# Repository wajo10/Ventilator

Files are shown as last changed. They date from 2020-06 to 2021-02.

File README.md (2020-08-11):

# RespiraWorks Open Source Ventilator












This is a common repository for all hardware and software components of the RespiraWorks open source ventilator project.

**If you intend to contribute, please read our [wiki](https://github.com/RespiraWorks/Ventilator/wiki).**

[RespiraWorks](https://respira.works/) is a 501(c)(3) non-profit organization with over 100 contributors worldwide
working to rapidly develop, manufacture, and deploy a low-cost and open-source ventilator for communities under-served
by the global supply chain.

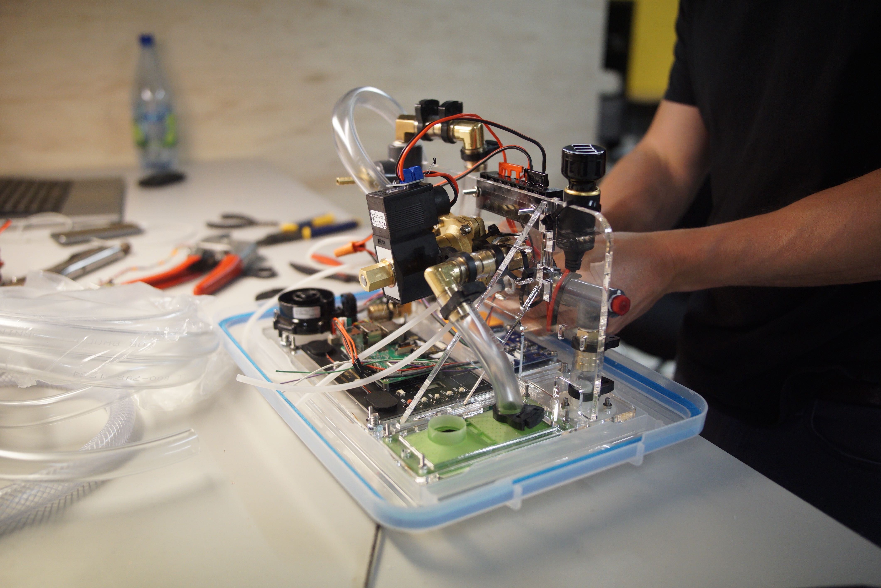
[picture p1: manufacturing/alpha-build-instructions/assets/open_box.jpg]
Ventilator under construction


## Design Origin

Most low-cost ventilator designs tackle the 'bridge' - how to keep a patient alive for 6-8 hours of closely monitored
care until they can be transitioned to a full ventilator. However COVID-19 patients require lung-protective adaptive
ventilation strategies, and require ventilator support for days to weeks.

Early in the crisis, we realized that the ventilator designs that could be completed in weeks might not be necessary,
and if so, a more feature complete ventilator would be needed. Despite constant developments in the disease progression,
we realized that a true-open source ventilator, with transparent requirements, design history documents, and yet still
optimized for low-cost and ease of manufacturing would enable expanded global access to a critical piece of medical
equipment.

Our ventilator exists between the short-term ambu-bag actuating designs and the commercial ventilators offered by
established manufacturers. It provides essential features such as a graphical user interface, adaptive pressure
controls, and fine control of FiO2, oxygen, and PEEP, with CMV, SIMV, PSV and PRVC operating modes. Unlike traditional
ventilators, our design work is being completed as fully open-source design, yet still with an IEC-conformant quality
process, and an optimized BOM for sourcing and manufacture worldwide.

Our target is not the US or Europe, but the middle- and low-income parts of the world that will deal with COVID-19 for
longer, with less healthcare, and a larger deficit of medical devices. RespiraWorks provides solutions for these
communities where existing manufacturers cannot.

## DISCLAIMER

**This is an incomplete, as yet untested design that is not yet intended to be used on patients.**

**This repository contains live documents. There are duplicate and alternative items for undecided aspects of the
physical design. Components may or may not connect and integrate as intended. Contents may also be out of date. If you
decide to buy or build anything, do so at your own risk.**

## CoVent Documentation

A set of comprehensive documents denoting the current state of the ventilator design, manufacturing and assembly specs,
was created for the CoVent competition in June 2020. Links to key documents follow. This is more detailed than the
documentation contained in the repository, but note that it is also a snapshot in time as of late June 2020.

* [Design Overview document](design/assets/covent-june-2020-design-overview-document.pdf)
* [Progress Status Report](design/assets/covent-june-2020-progress-status-report.pdf)
* [Assembly instructions](manufacturing/assets/covent-june-2020-assembly-instructions.pdf)
* [Manufacturing for custom components](manufacturing/assets/covent-june-2020-production-methods-for-custom-components.pdf)

## Repository Structure

* [System Requirements](requirements) -
  describes the requirement architecture, hierarchy, and process. Links to the releases of our system requirements, hardware specifications, and software requirements.
* [Ventilator Design](design) -
  describes the functional implementation and design theory of the system. This document also defines the hierarchy for the subsystems below.
    * [Design Rationale](design/design-rationales.md) - An explanation of the rationale that went into specific parts can be found here.
    * [Pneumatic System](design/pneumatic-system)
    * [Electrical System](design/electrical-system)
* [Manufacturing design](manufacturing)
    * [Alpha Build Instructions](manufacturing/alpha-build-instructions) - documentation for building the "Alpha" prototype of the device which can be used by contributors to test and experiment with.
    * [Beta Build Plan](manufacturing/beta-build-instructions) - Details on this page will be added as we progress further into beta build.
* [Printed Circuit Board (PCB)](pcb) - design, materials, assembly instructions, validation code
* [Ventilator Software](software) - Source code for cycle controller and user interface; debug tools, test scripts and test data
* [Research & Development](research-development)
    * [Project: Fan](research-development/project-fan)
    * [Project: IAV Air Control](research-development/project-iav-air-control)
    * [Project: Pinch Valve](research-development/project-pinch-valve)
    * [Project: Venturi](research-development/project-venturi)
    * [Characterization Test Plan](research-development/characterization-test-plan.md)
* [Quality Assurance](quality-assurance)
    * [Testing](quality-assurance/testing)

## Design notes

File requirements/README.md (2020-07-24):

# Requirements

We formally manage our product requirements in
[Valispace](https://covent-19.valispace.com/specifications/requirements)

For access and guide on using Valispace efficiently, see the [Using Valispace](using_valispace.md) page.

Latest exports:
* [PDF format](system-reqs.pdf)
* [XLSX format](system-reqs.xlsx)
* **#TODO:** export to `json`

## Managing requirements

This is a living document, the entry point for learning how we manage requirements and how to help with that. If you
learn something useful, or if you think this page could be structured better, **please edit this page**.

As usual, where appropriate, **cross-link with other resources**: e.g. Slack threads where a decision was made (or names
of people who made a decision), Github issues tracking certain work etc.

## Are the requirements up to date?

Not yet, but we're trying to get there: many of them need clarification, many are missing, some may be vague or
redundant. If something looks off, it probably is - please do your part to clarify it and edit the requirement - see
below how.

## Is everything in Valispace?

As of May 19, system and software requirements have been transferred from various spreadsheets on Google drive.
The deprecated sources of this transfer are available for reference in
[this folder](https://drive.google.com/drive/folders/10EUN9lYFaMPZbI094FU3wP_rDw2_dcRc?usp=sharing).

**TODO:** Have electrical / PCB requirements been transferred?

Some additional artifacts are highly related to requirements or should be cross-linked with them, but are currently not
managed in Valispace:
* **Failure Modes and Effects Analysis (FMEA)** - currently managed in
[this spreadsheet](https://docs.google.com/spreadsheets/d/1qlTV5HqxnhlJXuhbSsEIfU-YwnN6PzgASv9_2dc5-cM/edit#gid=929514620)
  * **TODO:** How do we manage cross-linking between FMEA and the requirements?
  * **TODO:** We should have a wiki page explaining the FMEA
* **Validation logs** - when we have a formal validation effort spun up, we will need to be able to trace every
requirement to logs of tests showing that the requirement is met in a specific version of the product.
* **TODO:** Anything else?

## Where did they come from?

The **system requirements** come from a variety of sources: ISO standards (**TODO:** which ones?), ventilator manuals
(**TODO:** which ones?).

The **software requirements** are a result of people from the Software team analyzing the system requirements from their
perspective and mapping them onto the software architecture
(**TODO:** we should have a page about software architecture).

**TODO:** Where did the other ones come from?

## How will we know that they are correct and complete?

**TODO:** How?

## How will I know when a requirement changes?

**TODO:** How?

## I have a general question about managing requirements

Ask it on `#requirements`. (**TODO:** Are there more detailed places where one should go with more specific questions?
Eg. hardware requirements, legal requirements, what to do if you need to talk to a doctor to clarify something?)

## I need to clarify an existing requirement

Use the Valispace "discussion" feature on the respective requirement.
**TODO:** Describe the feature in more detail, e.g. will I get a notification if somebody responds? Will I get a
notification if somebody asks a question about a requirement I added?

## I need to add a new requirement

If you found out that the system needs to have some important requirement that is currently not tracked, please add it
to Valispace and link it with other related requirements. For example, if you looked at the requirement "must have a
BATTERY LOW alarm" and found that there is no requirement to have a battery sensor, go ahead and add a requirement to
have a battery sensor.

If you're adding a new hardware requirement, ping David Gerson on Slack and let him know.

## Which requirements are higher-priority?

**TODO:** This ideally should link to a well-prioritized "milestones" page

# Cross-cutting TODOs

In addition to the explicitly listed questions on each requirement, a few recurring themes implicitly apply to almost
every requirement. We need to conduct several large-scale requirement cleanups.

* For all requirements we need to know which modes are they relevant to
  * **TODO:** How will we represent this in Valispace?
  * **TODO:** Classify all requirements by modes where appropriate - **should file a Github issue to track this**

* Many requirements talk about displaying a value, or a value being within certain bounds. It is often unclear whether
the value is an instant sensor reading, a computation from the most recent breath, a time series thereof, or an average
over some window (time-delimited or breath-delimited)
  * **TODO:** Audit all such requirements and clarify them -  **should file a Github issue to track this**

* Many values can be "commanded" (i.e. the device is trying to achieve a specific value) and "measured" (i.e. we can
measure what value has actually been achieved). In some requirements it is unclear which modality it is talking about.
  * **TODO:** Apply either "commanded" or "measured" to all magnitudes in all requirements - **should file a Github issue to
  track this**

* Requirements for device performance (how quickly and how precisely the device should achieve commanded values of
different parameters) are incomplete. There is a catch-all of 10% (**TODO:** insert ID for this requirement).
  * **TODO:** Identify such requirements for all necessary parameters - **should file a Github issue to track this**

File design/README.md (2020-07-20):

# System Architecture

-------------

This document contains description of ventilator design implementation and closure of issues which
apply at the system level, such as architecture configuration.

## Overview

A ventilator is a device which supports the breathing of a patient who cannot generate
sufficient respiratory effort to oxygenate their blood. In order to do that, the device
must generate sufficient pressure to overcome the resistance of the lung tissue and the
machine itself. It must vary this pressure over time as the lungs fill and then deflate.
In order to improve oxygenation, ventilators also almost universally apply some
back-pressure to the lungs (PEEP).

There are dozens of ways to design a ventilator and each has trade-offs. This document
describes the series of design decisions that led to the final design implementation
as a means of gaining a finer understanding of the final solution and why it resulted the
way that it did.

The first question is where the ventilator is generating pressure to drive into the lungs.

Displacement type devices provide a mechanical compression of a fixed volume to drive air
into the lungs. These are commonly employed in existing ventilators, and they provide a
high degree of volumetric accuracy and precise control of flow. There are two challenges
here. First is a question of supply chain, the volume of air which must be delivered into
a lung is relatively large, as far as traditional cylinders go. The lubricant and gasket
material must be oxygen compatible, and relatively expensive and sensitive drive
mechanisms are required. The designs end up rather heavy and expensive. Bellows-type
devices can be helpful in addressing the volume issue, but are very challenging to design
for the millions of cycles required, in addition to being difficult to source.

Ventilator Design Overview

[Source](https://docs.google.com/presentation/d/1ye96itSLfdbO9PQT0MSiq6xR2ArqD2MpV1Wj8ORfHeo/edit#slide=id.g7330d84036_1_0)

## Overview Documents

* [Concept of Operations](conop.md)

## Subsystems

**#TODO:** Introduce each subsystem properly

   * [Pneumatic design](pneumatic-system)
   * [Electrical design](electrical-system)
   * **Mechanical design: #TODO**

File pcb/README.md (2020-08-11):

# RespiraWorks Ventilator Mainboard Rev 1.0 

## Important Rev 1.0 PCB Errata
* [#63](https://github.com/RespiraWorks/pcbreathe/issues/63): DNP resistors populated on board, typing 3.3V to the 5V rail (bad) - if you have SN 01, 02, 03, or 05 - don't continue using the board without executing the fix in this issue ticket.  See ticket for rework instructions and photos.  All other serial number boards are shipping with this issue fixed.
* [#64](https://github.com/RespiraWorks/pcbreathe/issues/64): Yellow and Green alarm LEDs don't work due to a pin use conflict on the nucleo
* [#56](https://github.com/RespiraWorks/pcbreathe/issues/56): Blower command is 5V but nucleo outputs 3.3V.  All boards are currently shipping with a level translator fitted which addresses this problem, however the blower will turn on full blast briefly at reset ([#62](https://github.com/RespiraWorks/pcbreathe/issues/62) - to be fixed in next rev)
* [#66](https://github.com/RespiraWorks/pcbreathe/issues/66) I2C sensor connectors labeled A, C, B, D. Should be A, B, C, D :facepalm:  To be clear, what this means is, the I2C multiplexer assignments, as labeled on the board in Rev 1.0 are: MUX0: SENSOR A; MUX1: SENSOR C; MUX2: SENSOR B, MUX3: SENSOR D
* [#846](https://github.com/RespiraWorks/Ventilator/issues/846): anti-miller caps C33 and C34 filter out PWM signal and prevent proper operation.  The Miller effect is only present at startup and doesn't cause a problem with permanently connected loads like the PSOL.  Remove C33 and C34.

## Rev 1.0 PCB Quick Start Guide (visual guide pictures to be uploaded soon)
* If you have SN 01, 02, 03, or 05, make sure you check the errata above before you proceed or you may damange the Rpi.
* Verify that you have an STM32-L452RE module (not an STM32-L452RE-P module, they have different pinouts - see #51)

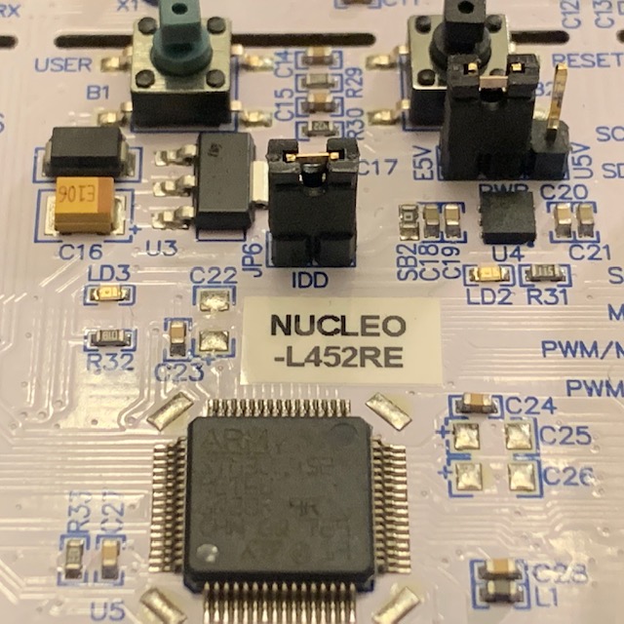
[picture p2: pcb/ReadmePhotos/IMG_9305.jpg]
verify model

* Plug the Nucleo into the PCB, observing the silkscreen (white outline on the board) for correct orientation.

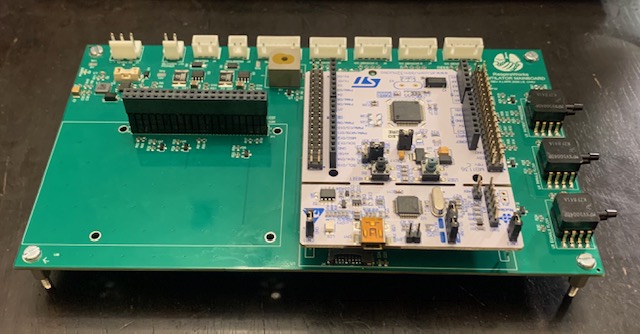
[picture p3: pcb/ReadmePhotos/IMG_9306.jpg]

* Move the JP5 jumper in the upper-middle-center of the Nucleo board to the E5V position.  This tells the board to expect external power from the PCB.  This will avoid programming problems.  If you wish to remove the Nucleo board and work with it on its own without the PCB, move the jumper back to the U5V position to power it from USB.

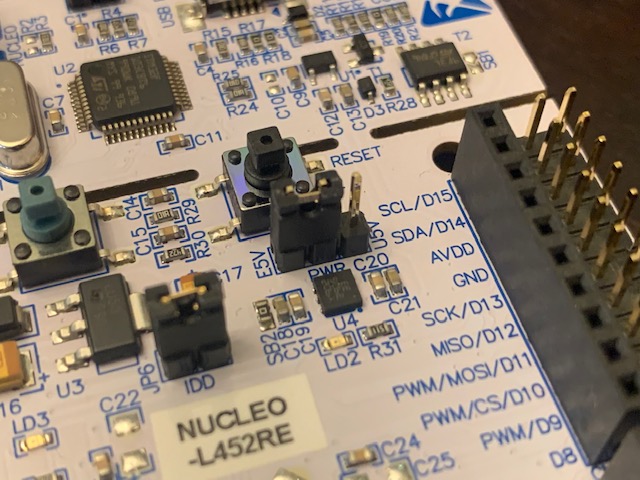
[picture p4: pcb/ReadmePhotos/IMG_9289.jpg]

* If you have a X-NUCLEO-IHM03A1 or X-NUCLEO-IHM02A1 stepper driver accesory, plug that in on top of the Nucleo.  The long gold pins of this module can get bent so make sure they are straight and they all go into their respective sockets successfully.  The stepper driver green connectors go in the direction of the white connectors on the mainboard PCB.  For setting up multiple stepper boards and/or connecting actual steppers, see "Setting Up To Drive Steppers" lower down in this readme.

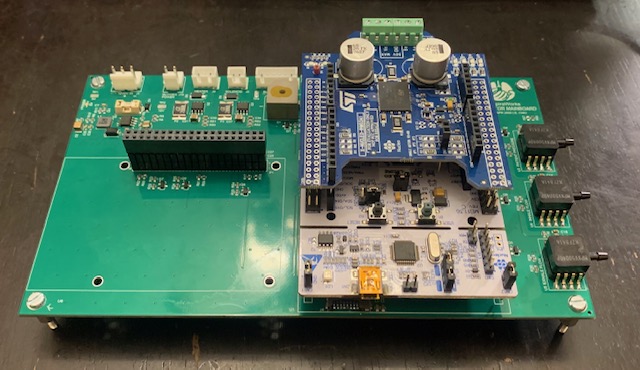
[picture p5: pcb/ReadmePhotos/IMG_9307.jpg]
plug in the stepper driver

* If you are using an Rpi 3B+ or 4 with this PCB, plug this into the RPI socket.  Note that if you have the standoffs fitted, do not overtighen them as this can damage the Pi.

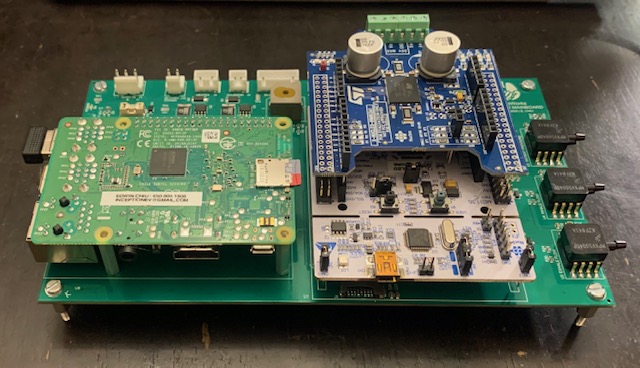
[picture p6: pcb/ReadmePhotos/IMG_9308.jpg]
plug in the Rpi

* If you are using Touchscreen w/ Speakers with your Rpi, connect an HDMI cable (included with Touchscreen package) between the Pi and the Touchscreen.  Similarly, connect a USB micro cable (included with Touchscreen package) between the Pi and the TOUCH+5V connector on the Touchscreen.

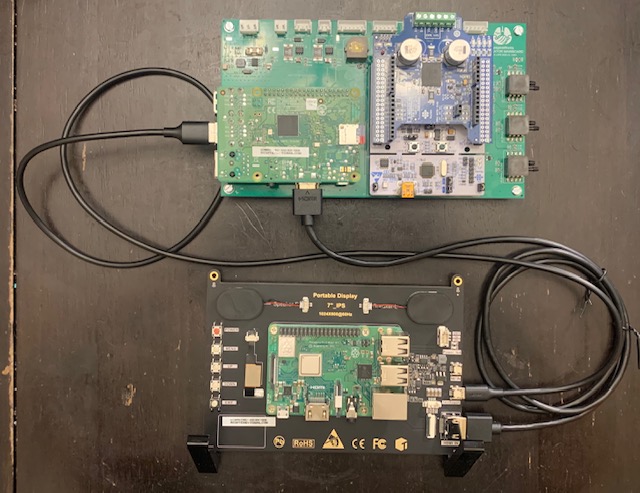
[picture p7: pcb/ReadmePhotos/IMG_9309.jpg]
plug in the Touchscreen

* If you are connecting a blower, take the 6-pin to 6-pin JST XH cable and connect it between the BLOWER CTRL connector at the top of the PCB with corresponding connector on the blower driver.  Likewise, take the 2-pin to 2-pin JST VH cable and connect it between BLOWER POWER connector at the top of the PCB and the corresponding connector on the blower driver.

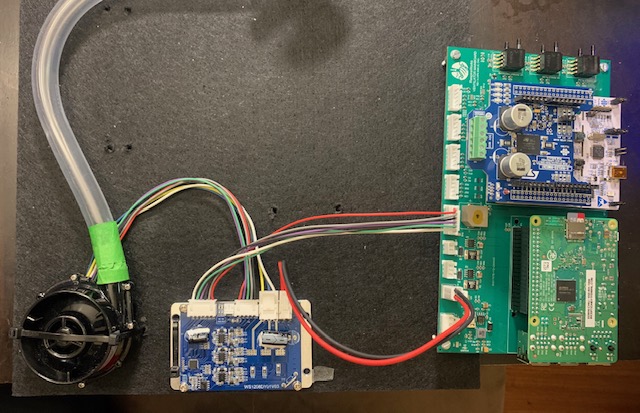
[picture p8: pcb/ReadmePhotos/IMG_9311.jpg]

* The PCB must be powered in order for the Nucleo to program correctly.  A power cable which plugs into the upper left corner of the PCB is provided with the board and allows it to be powered from any 12V, 1.2A or greater power adapter with a 5.5x2.1mm center-positive barrel jack.  You will want 5A or more if you are also powering solenoids, blowers, and heaters from the PCB.  Plug this in to the power the board.  A green POWER light in the upper left of the PCB should come on, and the various status lights of the Rpi and Nucleo will probably also come on.

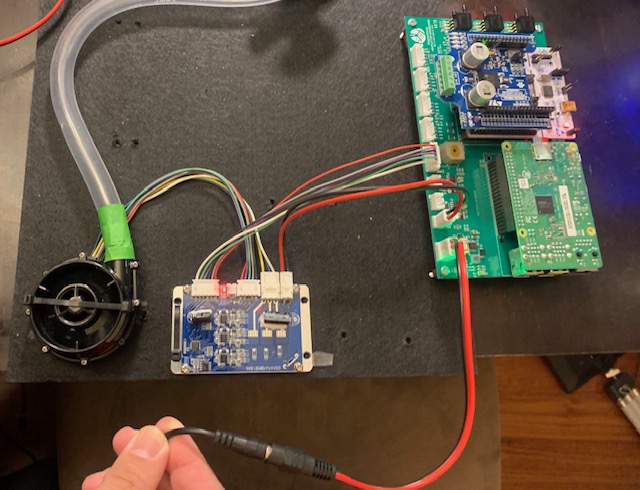
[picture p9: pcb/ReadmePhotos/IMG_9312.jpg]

* When programming over the Nucleo USB interface, the board emulates an ST-Link programming the MCU over SWD.  Use these settings in the toolchain of your choice.
* The bringup code was written in the Arduino IDE environment with STM32duino installed and can be found here along with basic instructions for setting up STM32dino and programming the STM32. (disclaimer: this code is not part of the project and is pretty much unsupported, use at your own risk.  The listing of hardware pin #defines at the top might be useful): [pcbreathe-bringup](https://github.com/inceptionev/pcbreathe-bringup)
    * for more test code with a state machine for running a ventilator setup in closed-loop control mode, see: [FMLtest] (https://github.com/inceptionev/FMLtest)
* The main reference for pin and GPIO assignments on this board are in the [Electrical Hardware Requirements and PCB Interface Control Document](https://docs.google.com/spreadsheets/d/1JOSQKxkQxXJ6MCMDI9PwUQ6kiuGdujR4D6EJN9u2LWg/edit?usp=sharing)
* The large power connectors on the PCB are JST VH type.  [Purchase Link](https://www.amazon.com/gp/product/B07LBZ3LCR)
* The smaller peripheral connectors on the PCB are JST XH type.
  * [Purchase link for 2/3/4/5-pin](https://www.amazon.com/gp/product/B06ZZ45G7G)
  * [Purchase link for 5/6/7-pin](https://www.amazon.com/gp/product/B079MJ1RYN)
* Here is a crimper that can crimp both types of contacts.  [Purchase Link](https://www.amazon.com/gp/product/B01N4L8QMW)
* The buzzer requires an oscillating signal to make sound, it is designed for peak output at 2.4kHz.  Take off the kapton cover at your own hearing risk.
* On the MPXV5004DP differential pressure sensors, the upper port is the positive measurement, and the lower port is the negative.  The transfer function, assuming a 12-bit ADC, is P[kpa] = ADCcounts/819 - 1
* The switched heater and solenoid outputs can support a resistive or inductive load up to 2A.  Refer to schematic for pinouts.
* The i2c sensor connectors are initially configured for providing 3.3V supply power to the sensors, but can be configured for 5V.  Each sensor can have its own voltage; they do not need to be the same.  If you need to switch to 5V, see the schematic for the resistors to change.  Refer to schematic for pinouts.
* The analog pressure sensors have an anti-aliasing filter value of 100Hz.

## Setting up to drive stepper motors
When the PCB was originally designed, the ability to add a stepper driver was essentially a hedge, a backup *just in case* we wanted to try something that required a stepper motor, so if some of this looks hackey, that's why.  Now that the stepper-driven valve concept is moving towards the main design, we need to support it.  This is the beginning of a guide to using stepper motors with the PCB, which will be completed in the following few days.

* This will assume some knowledge and practice with electrical tinkering.
* For bakground on stepper motors in general, the always-excellent Great Scott provides a good [intro to stepper motors](https://youtu.be/bkqoKWP4Oy4)
* For information on the powerSTEP01, the specific driver for X-NUCLEO-IHM03A1 we are using in Rev 1.0 of the PCB, [there is a video here](https://youtu.be/_Arx5CMr_mk).  Keep in mind that while this driver will stay for the duration of the Beta phase, we may move to something different in the final product, as powerSTEP01 is likely to be **way** overkill for this application, but it does offer a lot of convenient features.
* We will need to solder some wires to power the stepper driver as it takes a power input for the motor that is separate from the logic power it gets from the Nucleo below. We will piggyback off the blower driver power socket.  Solder two 13cm wires of 22awg or thicker to the backside of J10, the blower power connector. The square pin pad is negative.

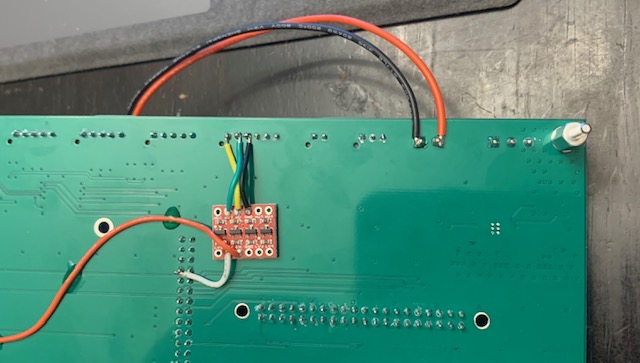
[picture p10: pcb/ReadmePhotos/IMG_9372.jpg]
solder power connection

* If you are using the X-NUCLEO-IHM02A1, before going forward, you have to change the board configuration to make it compatible with the PCB setup, using your trusty soldering iron:
    * Move the 0 Ohm resistor from SB34 to SB12 to connect PA5 to the clock
    * Move the 0 Ohm resistor from SB23 to SB8 to connect PB6 to CS
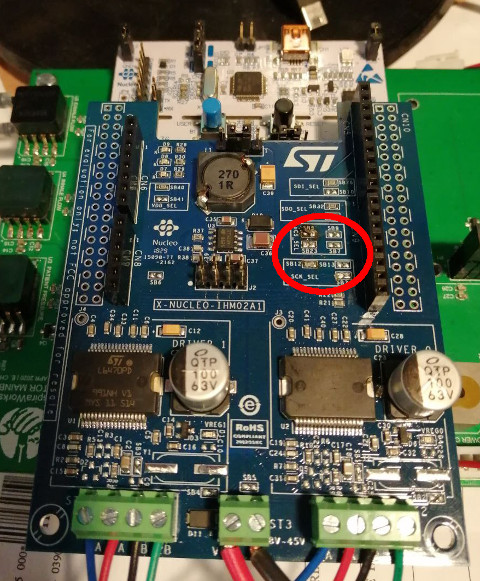
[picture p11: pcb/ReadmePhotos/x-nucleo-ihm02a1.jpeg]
X-NUCLEO-IHM02A1


* While we could put the wires of the stepper directly into the terminal block on the driver, making a little doodad like this will make it quick and easy to swap out different steppers that use this common 4-pin dupont 0.100" pitch connector.

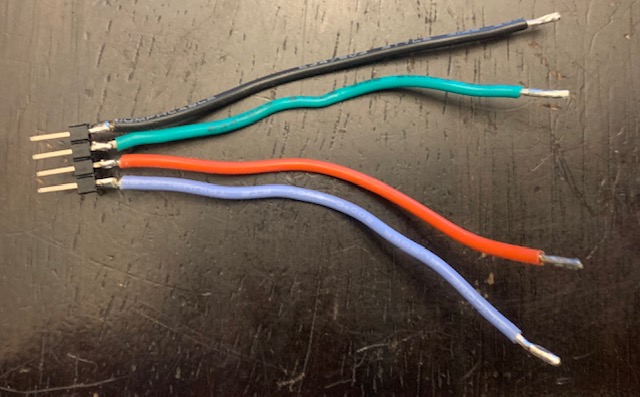
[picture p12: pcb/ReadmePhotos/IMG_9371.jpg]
terminal block wires


* Insert the wires in to the terminal block and connect them like so (note the example below is for the X-NUCLEO-IHM03A1, IHM02A1 is slightly different).  Screw them down to ensure a secure connection.

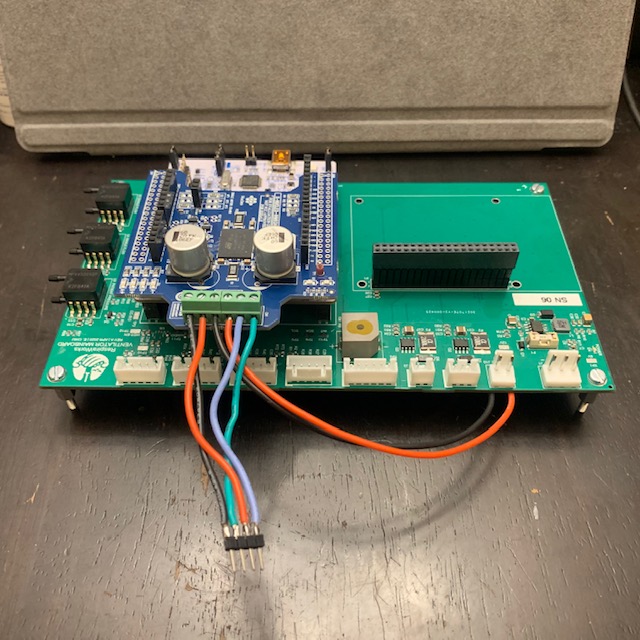
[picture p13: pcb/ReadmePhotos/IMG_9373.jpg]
screw down wires

* Connect the stepper motor to this connector.

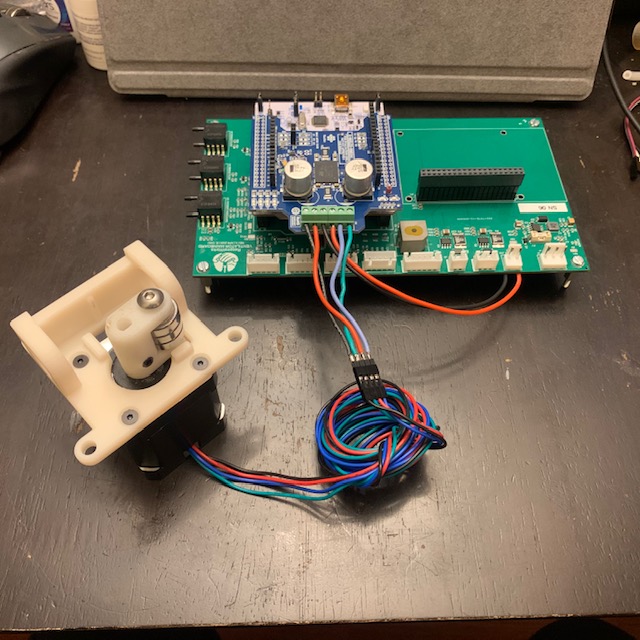
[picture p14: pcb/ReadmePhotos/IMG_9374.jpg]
connect stepper

* Note pin naming conventions and color codes vary from manufacturer to manufacturer.
    * If it does nothing and draws no current, swap one wire from the A pair with one wire from the B pair.
    * If you send a CW command and it turns CCW, then swap the polarity of either the A or B pair, but not both.
* Set the correct chip select for the powerSTEP01 (see [Hardware ICD](https://docs.google.com/spreadsheets/d/1JOSQKxkQxXJ6MCMDI9PwUQ6kiuGdujR4D6EJN9u2LWg/edit?usp=sharing) for pin assignments)
* Send SPI commands to the powerSTEP01 from the NUCLEO to setup the motor settings. [sample code: pcbreathe-bringup](https://github.com/inceptionev/pcbreathe-bringup)
* Send SPI commands to the powerSTEP01 to command motions. [sample code: pcbreathe-bringup](https://github.com/inceptionev/pcbreathe-bringup)
* Once you get one stepper motor working, and you are ready to use multiple stepper drivers, for X-NUCLEO-IHM02A1, you only have to connect the second stepper motor, but for the X-NUCLEO-IHM03A1, there are some more steps:
    * Consult the [X-NUCLEO-IHM03A1 user manual](https://www.st.com/resource/en/user_manual/dm00206777-getting-started-with-the-high-power-stepper-motor-driver-expansion-board-based-on-powerstep01-for-stm32-nucleo-stmicroelectronics.pdf) for information about how to stack the boards.  A brief overview of the process follows, but read the manual first.
    * Make the same motor connector doodad for the second board and install it.  Also prepare two short red and black power wires to piggy-back the motor power input.
    * You will need to move some resistors.  The manual link above will list which ones.

    * BOTTOM BOARD IN THE STACK (of two-board stack):

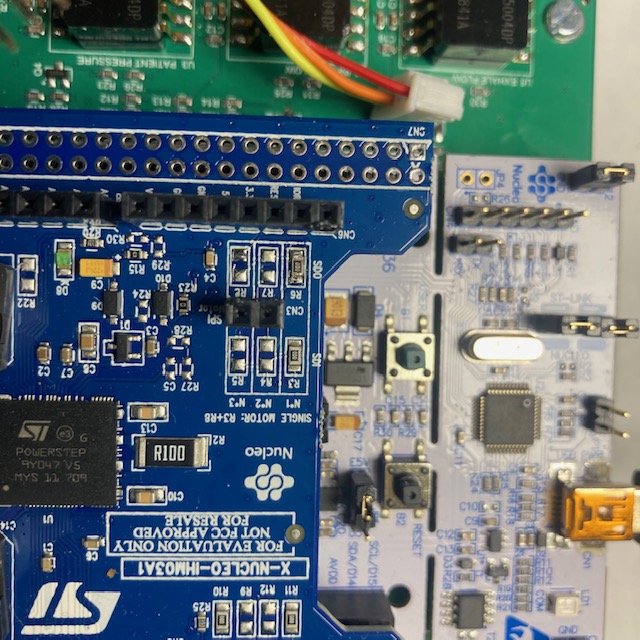
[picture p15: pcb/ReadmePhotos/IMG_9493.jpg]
bottom board
    

    * TOP BOARD IN THE STACK (of two-board stack):

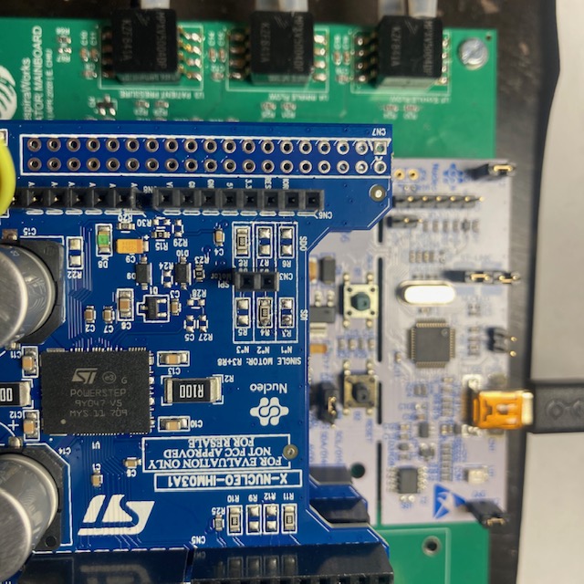
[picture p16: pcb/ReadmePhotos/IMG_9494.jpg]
top board
    

    * Put the two short power wires into the bottom board's power inputs along with the existing wires and screw then down.
    * Stack the boards, making sure that the long pins go into all their intended sockets.  They tend to get bent and might need some straightening.
    * Screw the two power wires into the upper board.

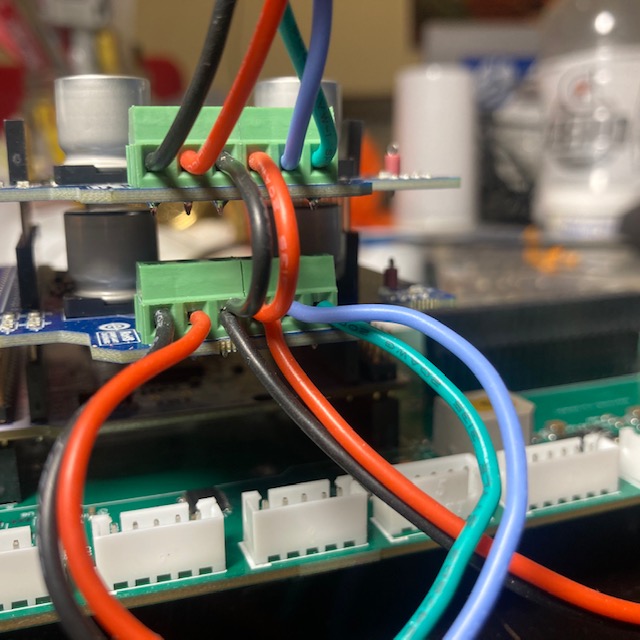
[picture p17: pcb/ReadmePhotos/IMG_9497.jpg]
power stack
    

    * You're done!  Plug in your motors and get moving!

    dual motors moving

## Rev 1 As-Built Files:
As-built directory: <br>
https://github.com/RespiraWorks/pcbreathe/tree/master/NIGHTLY/20200424v2-RELEASE-CANDIDATE-2

As-built Schematic: <br>
https://github.com/RespiraWorks/pcbreathe/blob/master/NIGHTLY/20200424v2-RELEASE-CANDIDATE-2/20200424v2-RespiraWorks-Ventilator-Rev1.0-RC2-DWG-SCH.PDF

As-built 3D STEP file: <br>
https://github.com/RespiraWorks/pcbreathe/blob/master/NIGHTLY/20200424v2-RELEASE-CANDIDATE-2/20200424v2-RespiraWorks-Ventilator-Rev1.0-RC2-3D-STEP.step

Manufacturing Pacakge: <br>
https://github.com/RespiraWorks/pcbreathe/blob/master/NIGHTLY/20200424v2-RELEASE-CANDIDATE-2/20200424v2-RespiraWorks-Ventilator-Rev1.0-RC2-PKG-TURNKEY.zip

## Requesting Hardware for Dev:
Request hardware by making an entry here: https://docs.google.com/spreadsheets/d/1rf-cOTlQL_LnzrZq-64n7_R_pFyFMdCAxsPC65YqKUg/edit?usp=sharing

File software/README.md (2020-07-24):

# Ventilator Software

This directory contains the source code for the ventilator software, test code, sample data and debug utilities.

## Contents

* [design](design) - documents on software architecture and requirements
* [common](common) - code common to both controller and GUI executables
* [controller](controller) - code for pneumatic system controller (stm32)
* [gui](gui) - code for the ventilator graphical interface (Qt)
* [sample-data](sample-data) - sample data for offline testing and recorded performance test data
* [utils](utils) - scripts for debugging controller and mocking communications interface

To contribute, please first read the [onboarding page](https://github.com/RespiraWorks/Ventilator/wiki).

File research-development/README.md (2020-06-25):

# Research & Development

## Overview

This contains projects for ventilator components that are actively being researched and developed.

## Projects

* [Fan](project-fan)
* [IAV Air Control](project-iav-air-control)
* [Pinch Valve](project-pinch-valve)
* [Venturi](project-venturi)

## Characterization Testing

For details and characterization test data, see the [Characterization Test Plan](characterization-test-plan.md).

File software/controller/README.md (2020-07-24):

# Ventilator controller software

Here resides the code for the ventilator controller.

## High-level graph of components

<!-- See https://github.com/TLmaK0/gravizo -->
Graph of components in cycle controller
<!--
cc_graph_mark
digraph G {
  subgraph cluster_RPI {
    label="GUI (Raspberry Pi)"
    labelloc=b;
    GUI [label="Qt app"]
  }

  subgraph cluster_CC {
    label = "Cycle Controller (STM32)";
    labelloc = b;
    "Main loop" -> "Controller"
    "Main loop" -> "Comms"

    "Controller" -> "Sensors"
    "Controller" -> "Actuators"
    "Controller" -> "Breath FSM"

    "Actuators" -> HAL
    "Sensors" -> HAL
  }

  "Comms" -> GUI
  GUI -> "Comms"
}
cc_graph_mark
-->

Please also see the [Software design pages](../design) for more information on controller architecture.

## Rationale and structure

The ventilator actuators must be driven by control loops ensuring continuous
breathing according to doctor-provided parameters, while also ensuring
no harm is done to the patient.

Controller code is separated from the user interface code. This makes the code base
smaller, easier to maintain, and lessens the risk of unexpected behavior.

The controller shares the [common communications code](../common) with the GUI.
The part of the code specific to the controller resides here.

**Directories:**
* [lib](lib) - most of the substantive controller code, must all be libraries to be unit-testable by platformio
* [test](test) - unit tests
* [integration_tests](integration_tests) - code for (semi-)automated hardware-in-the-loop testbeds
* [platformio](platformio) - build configurations and deployment scripts
* [src](src) - just the main loop for controller
* [src_test](src_test) - just the main loop for unit tests

**Files:**
* [platfomio.ini](platformio.ini) - the equivalent of a "make file" which governs how platformio builds targets
* [controller_coverage.sh](controller_coverage.sh) - script for generating unit test code coverage reports
* [test.sh](test.sh) - script for running all unit tests
* [upload.sh](upload.sh) - uploads firmware to ventilator controller

## Development toolchain

The target platform for this code is the STM32 processor (currently, the Nucleo L452RE to be precise).

We use [platformio](https://platformio.org/) for building the controller code.
Platformio has a CLI and an IDE. You'll need the platformio CLI in order to build
from the command-line, even if you also install the IDE.

Instructions for installing:
 * [CLI](https://docs.platformio.org/en/latest/core/installation.html#super-quick-mac-linux)
 * [IDE](https://docs.platformio.org/en/latest/integration/ide/vscode.html#installation)

In case of unix systems, the `pip`-provided platformio package tends to be more up to date, so opt for that over `apt`.

Here's a [video introduction](https://www.youtube.com/watch?v=EIkGTwLOD7o) to platformio.

PlatformIO works on Windows as well.
You'll need to install [Atom](https://atom.io/),
[Clang+LLVM](https://releases.llvm.org/download.html),
and [Python](https://www.python.org/downloads/windows/).
(Note: you may be asked to install Python 2.7, but PlatformIO works with Python 3.5+ as well, ostensibly.)

## Building and testing

After installing platformio, you should be able to build and test as follows.

```
$ ./test.sh
# This will run a few commands, such as "platformio run" and
# "platformio test -e native".
```

This is the same script that runs on our continuous integration server (Travis CI).
Run it frequently during development to catch errors/style violations early.

Sometimes PlatformIO can get into a bad state -
e.g. if things don't build for you in `master`, try:

```
$ rm -rf .pio/
```

## Running on the controller

To run this you will need at a Nucleo dev board and/or some version of the PCB.
For various builds of the physical system, please refer to the `system-design`
folder in this repository.

Plug in the STM32 to your machine, then ask platformio to list all devices connected.
You should see a USB serial port corresponding to your device.

```
$ pio device list
/dev/cu.usbserial-14220
-----------------------
Hardware ID: USB VID:PID=1A86:7523 LOCATION=20-2.2
Description: USB2.0-Serial
```

Now you can build and upload to the device.
**Note:** The following command should be run in this directory (same as where `platformnio.ini` lives).

```
$ pio run -t upload
```

A more convenient way to run is to use the [upload.sh](upload.sh) script. If you have multiple Nucleos that you
want to deploy to, you should consult the [platformio configuration guide](platformio).

If you get the following error, it means platformio was unable to find a connected device.

```
# This means pio couldn't find a device to upload to.  Check that it's connected?
Error: Please specify `upload_port` for environment or use global `--upload-port` option.
```

You may have to modify your `udev` rule to enable flashing of the controller as follows:

```
curl -fsSL https://raw.githubusercontent.com/platformio/platformio-core/master/scripts/99-platformio-udev.rules | sudo tee /etc/udev/rules.d/99-platformio-udev.rules
sudo service udev restart
sudo usermod -a -G dialout $USER
sudo usermod -a -G plugdev $USER
```
and then either re-login or restart machine.

For more details on this, see the following articles:
[platformio FAQ](https://docs.platformio.org/en/latest/faq.html#platformio-udev-rules)
[community forums](https://community.platformio.org/t/stm32-vs-code-mbed-upload-issue-error-libusb-open-failed-with-libusb-error-access-error-open-failed/10650)

Alternatively, you can upload the firmware.elf and firmware.bin files to the controller mounted as a USB storage device.

## Testing with hardware

Some (semi-)automated integration tests are in the [integration_tests](integration_tests) directory.

Debug interface and manual testing utilities are in the [../utils](../utils) directory.

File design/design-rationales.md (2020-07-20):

# Design Rationales

NOTE: The documentation below is a summary. Comprehensive details on design rationale for the entirety of the ventilator  (updated for CoVent as of June 2020) is [available here](assets/covent-june-2020-design-overview-document.pdf).

## Overview

This file is meant to document the rationales for the design decisions we're making - or things we considered and rejected.

Caution: this document has not been formally reviewed and is a work in progress. Be responsible to
understand the provenance of documentation.

Also note: right now we are collecting initial information here since it is easier - we may split
this up to have the different sections live with the different component folders, but we'll figure that out later.

## Guiding Principles

1. **Low cost but robust and safe** - we want to create something that is affordable, but also that can perform the necessary
duties reliably with high confidence over extended periods of time. The goal is to satisfy external specifications for ventilator requirements - but also assess the cost of the requirements and not blindly follow them if it drives big decisions in the system.

2. **Keep It Simple (Stupid)** - remove complexity wherever possible to reduce failure modes (and cost), without sacrificing key functionality (though certain functionality may not be achieved)

3. **Make it something that doctors will use** - it won't necessarily do everything, but we want the ventilator to provide the key needs of doctors. Therefore, we must keep doctors extremely in the loop and constantly get feedback from them on what we're doing.

4. **Amenable to developing world supply chains and maitenance** - don't presume that the medical context we might be used to is the same in our target market. The only way to get this information is contact with doctors and workers familiar with the facts on the ground.

5. **Open source** - we want this project to be something that anyone who wants can build off of and leverage. Therefore, all designs, rationales behind those designs, requirements, processes, etc. will be documented in a common repo that everyone has access to. **#todo** - go through and make sure all of the links in here are in git so that people can access them (some slack links exist temporarily before the information is fully resolved and moved to git)

## System CONOPS/System Design

More detailed thoughts on this [here](conop.md).

* Targeting **pressure control** for two reasons:
    1. We got early feedback that this was most important to doctors - though we have gotten feedback that volume control is also important.
    2. A lower cost pressure controlled system seemed more achievable - and theoretically a good pressure controlled system should be able to do volume control. Currently we are pursuing pressure control and will be evaluating how accurate volume measurements we can get to determine if the design can also support volume control.

* **Doctors need fine control of FiO2** -> this drives the need for an oxygen supply, the need to support oxygen mixing and sensing, and the need for a variable state valve on the O2 supply to adjust the flow rate dynamically. **#todo** Need more info on the ox system design we pick.

* **Multiple closed loop (feedback control) systems create complexity by creating interacting dynamics** -> we're attempting to only have a single closed loop controlled part of the system at a time and to target one key feature (e.g. pressure with FiO2 achieved across cycles). We're also working to determine which components (e.g., valves, blower) need to be controlled and how in order to figure out what will actually support the system requirements.

* Anything that will be exposed to high oxygen contrations and pressures needs to be safe and ox-clean. This drives a desire to **reduce the number of items directly in the flow as much as possible**, especially for high-pressure (greater than 1 bar O2)

* **Air valve after the fan/blower with air valve being closed loop controlled and fan being open loop** -> The ventilator requires a high rise time of the pressure when transition from PEEP to PIP. A motor which can change the fan inertia this quickly against increasing pressure ends up being the fan for some high-performance ventilators, or expensive. We have solved this by the use of a proportional valve after the fan. The fan runs at constant power, and the pinch valve is used to modelate the flow. For refernce, one fan we got quoted was $500 and we were never able to get one delivered. A fan capable of meeting the pressure spec + an air valve capable of the rise time spec was less than $75.

* The goal is to maintain **some bias flow through the system at all times**, both to help the fan and to avoid big surges from completely opening and closing different parts of the circuit. This also helps ensure a 'one way' flow of particles and aids with sterilization.

* **Trigger breath transitions off of changes in flow instead of pressure** -> Because the ventilator is pressure controlled, it adapts to small changes in pressure by adjusting the flow rate (by adjusting the valve states) in order to maintain pressure. Therefore, changes in flow rate are a better sign that the patient is attempting to inhale or exhale. #todo need to confirm this/flesh this out as we go

* **Anti-asphyxiation design** (**#todo** need to confirm all this)
    * **Pneumatic** If the ventilator loses power, it is important that the patient is able to breathe and is not given dangerous amounts of pressure/flow. The oxygen system is fed by an external pressure source that the ventilator doesn't control; therefore, in the loss of power it is important to shut off flow from the oxygen system to keep the patient safe. We accomplish this by using a normally closed solenoid on the oxygen limb. The air/blower valve and the exhale valve are made to be normally open so that those paths are unobstructed to allow the patient to breathe.
    * **Electrical** To support the air/blower valves and exhale valves being normally open, the Cycle Controller watchdog timer is connected to the stepper motor drivers, which will default them to an unpowered state in the event of a Cycle Controller computing failure, causing the valves to snap open.

* **Use of stepper motors** - **#todo** need to fill this out

* **Metric vs imperial** - **#todo** fill this out when we make a decision

## Valves

* **Pinch Valve (Custom design)**
    * Low cost, robust design for achieving variable flow based on peristaltic tubing.
    * The valve mechanical components are not exposed to the flow, which means it is not exposed to high O2 concentrations directly.
    * Normally open, which is important for anti-asphyxiation in the case of power loss
    * Still evaluating fatigue and lifetime / sealing.
    * Originally designed as the exhale valve to give control for maintaining PEEP - under considering to use for both the air inlet and for the oxygen inlet
    * For more informatin about the design of this valve, see [here](../research-development/project-pinch-valve)

* **Idle Air Control Valve (IAC)**
    * Common automotive part that is cheap and widely available.
    * A linear stepper motor drives a pintle up and down to create a variable orifice.
    * Unclear how these valves perform in high O2 environments or if they could be sufficiently rated/cleaned.
    * Significantly cheaper, more robust, and more widely avaiable than the pinch valve.

* **Proportional Solenoid (PSOL)**
    * Relatively uncommon part but used in traditional ventilators.
    * Provides precise, reliable control of high-pressure gasses.
    * May be cost effective but requires a high-pressure source of oxygen (can not use low pressure sources like oxygen conentrators without a booster pump).
    * O2 cleaned PSOLs are relatively hard to find, though are already in use on ventilators. We may be able to clean automotive PSOLs.
    * Normally closed, which is important for anti-asphyxiation. **#todo** need to confirm this

* **One way valve (check valve)**
    * Needs to work in an O2 environment
    * Needs to be reliable and relatively low cost
    * Still figuring out the exact one way valve design
    * Two possibilities are a normal umbrella seat check valve, problem is these have a high cracking pressure. This could be OK on the intake side where the fan can generate this but would be a problem on exhale.
    * duckbill valves have also been explored, but these can chatter at low flow rates.
    * Could possibly modify a normal check valve by cutting the spring down or out.

* **Relief Valve**
    * **#todo** when we figure this out

## Tubing
* Pick peristaltic tubing in the pinch valves so that it can withstand many cycles
* Otherwise any biocompatible tubing is fine, gneerally Tygon for most of the testing.
* Needs to be O2 safe
* 3/4 inch standard allows relatively cheap fittings. Need to transition to metric for int'l.

## Sensors

* **DP sensors / Venturi**
    * The goal of the venturi design is to measure the flow through the system at a limited pressure drop and with a large signal.
    * Venturi's are nice because they are cheap and yet can provide reliable flow measurements. See [this ticket](https://github.com/RespiraWorks/Ventilator/issues/9) for info about evaluating the venturi's.
    * Currently we are using the difference between the two flow measurements (one for inhale and one for exhale) to determine the tidal volume delivered to the patient. We are still evaluating how to do this - see [this ticket](https://github.com/RespiraWorks/Ventilator/issues/57) for more information.
    * Another open questions is manufacturing of the venturis - currently the goal is to design a venturi that can be injection molded.
    * For more informatni about the venturi design, see [here](../research-development/project-venturi).

* **Patient Pressure sensors**
    * Needs to be reliable, handle many cycles, and meet the required ranges and accuracies of the requirements (#todo flesh this out more).
    * Currently only one sensor is used, but maybe a second one is required for reliability.

* **O2 sensor**
    * The O2 sensor needs to be able to measure up to 100% O2
    * Right now we are using a galvanic cell O2 sensor - but those are known to degrade quickly. [This ticket](https://github.com/RespiraWorks/Ventilator/issues/56) is tracking our discussions on this topic.

* **Mass flow sensor***
    * We have shied away from mass flow sensors because they are very expensive when compared to the DP sensor/venturi design. However, they are accurate and used on other system so they are not completely ruled out.

## Filters
* Filters on inlet/outlet to prevent contaminents from the surrounding environment getting into the device
* Filter on patient circuit to avoid device contamination and spreading particles between patients
* We're currently looking at HEPA filters since they are commonly avaible and cheap - but we're also evaluating other options. HEPA filters are appropriate because they are designed to filter small particles. [More info on HEPA filters](https://ntrs.nasa.gov/archive/nasa/casi.ntrs.nasa.gov/20170005166.pdf)
* 2 part mold for holding the filters is meant to be easily manufacturable and to allow easy changing of the filters over time
* Filters are placed physically on the outside of the box so they can be replaced without the box being opened

## Blower
* Current blower is not rated to 100% O2, which drives the lack of a blower on the O2 system and a one way valve in front of the blower to keep it separate from the high O2 part of the system
* We have evaluated a large number of blowers. When balancing supply chain, ubiquity of specification, and future avaialability, we settled on this one. However, there is an issue with the pressure spec for the fan. If we needed to reach 60 cm H2O, this fan might be under powered. We are currently leaning to not support those high pressures
* **#todo:** link to the fan we picked

## Enclosure
* Must be sterilizable
* Must be manufacturable with commonly available fabrication equipment in the markets we are assessing (currently targeting custom folded sheet metal)
* Enclosed to protect the internals and keep out dust
* Has an external fan for cooling the internal electronics
* Ruggedized and compatible with the hospital environment
* Must support easy assembly and maintenance of the various components

## Humidifier
* Currently planning to use an off the shelf external humidifier—see [this ticket](https://github.com/RespiraWorks/Ventilator/issues/704) for more details.

## PCB/Electronics

* **SRM32 Microcontroller For the Cycle Controller**
    * More powerful than the simpler arduino and Raspberry pis, but still cheap and widely available
    * Used in other medical devices
    * Comes with more powerful/extensive debugging tools
    * Familiar to many of the members of our team
    * See [this ticket](https://github.com/RespiraWorks/Ventilator/issues/709) for more details on why a STM32 microcontroller was chosen.
* **Rasperry PI and Rasperry PI Touch Screen for GUI**
    * Cheap and widely available
    * Existing libraries for touch screen interactions that can be leveraged
    * Has lower performance requirements than the cycle controller
* **Power Supply**
    * 12V standard chosen to ensure flexibility of power supplies (e.g. battery or UPC)
    * Open question on internal alarms battery
* **#todo** - need more here.
* **#todo** - add diagrams from design reviews and such

## Software

* **#todo** - add diagrams from design reviews and such
### Separation of UI Controller and Cycle Controller
* To maximize safety, it is important to minimize the amount of software that is immediately hazardous to the patient (can cause harm in <1s, making human intervention useless), and expose any hazardous software to high levels of verification and testing. By moving the UI code to a separate porcess, it reduces risk and saves time because the complicated UI code doesn't have to be exposed to the same verification and testing as the cycle controller.

* NOTE: Neither of the controllers are a complete backup for the other - this is not a redundant system.  If either fails in a way that is not fixed through the watchdog reset, an immediate intervention will be needed to keep the patient alive.  The objective in the case of either failure is to sound the alarm so that the intervention can happen - and to design the system such that in the event of a failure there is time to make an intervention.  Making a truly redundant system will add cost and time, and so has been deferred for now.

* **Watchdog Timers**
    * In the event of a computing failure in either the UI Computer or the Cycle Controller, a watchdog timer monitors each and will reset the offending computer, which should then be able to regain control of the valves.
    * **#todo** it will need to be confirmed in the final design that the UI Computer cannot command any modes that will cause the Cycle Controller to hold these valves closed.

### GUI / UI Controller
* **#todo** - needs more
* Items that fall within the UI Controller:
    * Cycle Controller Watchdog/Alarm
    * User Parameter Setting
    * Ventilation Mode Setting
    * Sensor Data Reporting
    * Respiratory Cycle Plot Display
    * Alarm Information Display
    * Alarm-specific alert sounds

### Cycle Controller
* **#todo** - needs more
* Items that fall within the cycle controller:
    * UI Computer Watchdog/Alarm
    * Closed-Loop Valve Control
    * Open-Loop Blower/Valve Control
    * Respiratory cycle Control
    * Sensor Data Reading
    * Sensor Failure Alarm
    * Overpressure Alarm
    * Respiration Rate Alarm
    * Broken Loop Alarm

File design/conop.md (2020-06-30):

# RespiraWorks Ventilator Concept of Operations (conop)

## Purpose

- Build a common understanding of ventilator internal operation amongst different parts of the team.

- Caution: this document has not been formally reviewed and is a work in progress. Be responsible to understand the provenance of documentation.

## Document Content

- Summary of key constraints
- Understanding of current intra-breath cycle control for the development (“Pizza”) board.
- Preliminary description of system operation for next iteration of system with O2 mixing
- Envisioned Inter and Intra-breath cycle control states
- Open questions / points to resolve.

## Functional Diagram

Functional Block Diagram

## “Pizza Build” Intra-breath Cycle Control

The Alpha system flow path is:
- Fan
- Air Valve (not on current pizza build)
- Tee <-> Test Lung
- Exhale valve
- Exhaust

The Alpha build (first iteration) did closed loop control on the blower speed and setpoint control on the exhale valve state to achieve the desired target pressure. However, this left significant shortfalls in both pressure rise and pressure reduction times.

The intra-breath control cycle for the Alpha build is:
- **Inhale:**
Increase pressure set point for closed loop control to PIP pressure
Exhale moves to exhale position (fully closed)
Controller adjusts blower speed based on PID control closed around the measured patient pressure
PIP pressure target is maintained for a specified amount of time - then step transition to exhale
- **Exhale:**
Exhale valve moves to exhale position (fully open)
Controlled adjusts pressure set point for closed loop control to PEEP pressure - controller adjusts blower speed to meet PEEP.
PEEP pressure target is maintained for a specified amount of time - then transition back to inhale

Alpha build has no inter-breath or “adaptive” control on top of this.

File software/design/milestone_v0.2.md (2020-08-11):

# This milestone is complete

_Information below only for posterity._

## How to use this page
This is a high-level overview of what we want to achieve for v0.2 (a.k.a Covent) milestone. Up-to-date state of its implementation
is [here](https://docs.google.com/document/d/1CHgz-y6wV6duTg66s1h8-wZZ6Tn22U1iL5WtjhSYQgk/edit#). Requirements are captured on Valispace.

## Date

Deliver to Covent by June 18th.

# Objectives
## Modes
 1. Pressure Assist Mode. That is mandatory ventilation together with inspiratory attempt detection.
 2. (stretch goal) High-flow nasal cannula (HFNC). Ventilator provides light continuous positive pressure, patient breathes on their own.
 3. (stretch goal) Pre-test mode (a.k.a. self-test mode).

Full description of all ventilator modes is [here](ventilation_modes.md).

## User Interaction

See [UI Requirements](UI_requirements.md).

## Alarms
We need 6 alarms that were in covent requirements:
1. Gas pipeline failure
2. Pressure exceeds
3. Apnea
4. Pressure not achieved
5. Tidal volume
6. Electricity supply failure

## GUI
Two new features have to be added for Covent:
1. Modes selection
2. Alarms settings

# Requirements

Requirements are captured in Valispace, tag v0.2

# Tasks
Specific tasks are captured as GitHub Issues in the following milestones:
 - [v0.2 GUI](https://github.com/RespiraWorks/Ventilator/milestone/12)
 - [v0.2 Alarms](https://github.com/RespiraWorks/Ventilator/milestone/11)
 - [Pressure Assist Mode](https://github.com/RespiraWorks/Ventilator/milestone/8)
 - **HFNC mode** - deleted milestone (August 2020)
 - (stretch) [Self-test mode](https://github.com/RespiraWorks/Ventilator/milestone/10)
 - (stretch) [v0.2 Controller](https://github.com/RespiraWorks/Ventilator/milestone/13)

# Brain dump, to be sorted and reorganized into sections above

We also need:
* Architecture / preliminary design review
* Calibration tools/modes for subsystems
* Validation testing plans for specific subsystems (this might be software or additional documentation overhead)
* Listing and managing the software-specific risks (note: this work is underway [here](https://docs.google.com/spreadsheets/d/1qlTV5HqxnhlJXuhbSsEIfU-YwnN6PzgASv9_2dc5-cM/edit?usp=sharing) by jam@)
* We need a software architecture review
* We need 1 or 2 people to help physical design team publish their content on github and document things in a colleague- and people-friendly way

Specific software designs needed:
* A design for alarm management ([Slack thread](https://respiraworks.slack.com/archives/C0100SF3N5T/p1589153203185000))
* A design for controller self-test mode ([Slack thread](https://respiraworks.slack.com/archives/C0100SF3N5T/p1589153203185000))
* Persistence (what to do if controller resets - start from blank slate? recover control state?)

## Robust testing and debugging
* A debugging interface - ability for developers to debug what's going on in more detail than the user-facing GUI provides
* Continuous Integration that runs tests on a real device:
  * Running unit tests against a device - which is also critical for validating the correctness of the HAL
  * Running integration tests against a full ventilator assembly
* Continuous Integration that builds a GUI image for RPi

## Simulated testing

We need simulated integration testing of physical scenarios such as "patient is hooked up" etc.

We have a sub-team of folks from Modelon who hang out on [#modelica](https://app.slack.com/client/T0102KRCH5M/C011HUP75EJ) and build a model of the system (ventilator + patient + controller) in Modelica, a language for simulating physical systems. We want to integrate our Controller with that model so we can simulate what would happen if the real ventilator was being controlled by it. See [these meeting notes](https://docs.google.com/document/d/14lrTVcYuuUii7QTvuJJneex-_uKSHQ33Hg9CR5pOARo/edit#heading=h.cpwphjtw2hj8) for more.

Can we check in regularly against Modelica to gain confidence that we're meeting functional requirements?

Contact persons:
* On Modelica side, John Batteh and Elizabeth Hillstrom.
* On Software side, Eugene Kirpichov

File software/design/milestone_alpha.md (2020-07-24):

# This milestone is complete.

_Information below only for posterity._

# Objectives
* Provide a physical proof-of-concept for demonstration and review with medical experts
  * See **Demo script** section below.

* Provide a platform for continuous engineering experimentation
  * E.g. Edwin will want to play with the thing with a test lung. Ideally the software should be conductive to that, e.g. have the parameters adjustable via UI rather than baked in.

# Requirements

* Must have a minimal GUI (graphical user interface) that can display pressure trace, flow trace, volume trace
  * GUI is ideally our specialized QT GUI, but if that's not ready by demo time, we can use [DEPRECATED LINK].
    * *jlebar*: That approach won't work with our current protobuf-based protocol.  We can change our code to output something parseable by that tool if necessary, but my preference would be to do something that we don't have to throw away.  For example, Albertas put together a [proof of concept Python script](https://github.com/RespiraWorks/Ventilator/commit/330895ea391ee70cf156fb5bd8673434b3908846) that reads protobuf data from the Arduino.  We could use an approach like this to draw graphs in Python.

* GUI must obtain pressure, flow, volume data from the controller
  * [Per Ethan](https://respiraworks.slack.com/archives/C012H3G1GQ5/p1587857837002500): Flow/volume do not need to be right, just look right:
  * Ideally, use sensor readings with calibration at device startup and smoothing
  * But for alpha, OK to do calibration once on the demo device and hard-code calibration parameters; omit smoothing
  * Absolute worst case, use synthetic data for demo

* Controller must implement Pressure Control (aka Command Pressure) mode
  * Defined in [this presentation slide](https://docs.google.com/presentation/d/1DA1BQlCj8wNv60pGGzrldPfZBmr6WAH4WbrD4W7i43U/edit#slide=id.g739b1a32cc_0_12), prototyped in [pid.cpp](https://github.com/RespiraWorks/Ventilator/blob/fee155d5d4e8fa029b2e83e4753cfaeb15b9b365/controller/src/pid.cpp), correct implementation tracked [here](https://github.com/RespiraWorks/Ventilator/issues/17)
  * Within alpha, for demo, controller can implement this autonomously, i.e. with parameters hard-coded in the controller rather than obtained from the GUI.
  * However, getting mode parameters from GUI is a nice-to-have, per objective 2 above.

* Must not crash irrecoverably or self-destruct.

# Demo Script
This is a narrative description of how we expect the alpha test to go.  We will probably be running a subset of the tests described in Appendix B of the [MHRA Requirements](https://assets.publishing.service.gov.uk/government/uploads/system/uploads/attachment_data/file/879382/RMVS001_v4.pdf).

* Hook up RespiraWorks Ventilator to a test lung
* Turn on device and begin showing data on a screen, either on the GUI or a laptop
* Run a set of respiratory cycles at default, middle of the range values.
* Adjust each of PIP, PEEP, I:E, and RR one at a time, starting from default values, while recording data.
* Run some of the more extreme corner cases involving two or more of the above settings (i.e. High PIP, low PEEP, Low I:E, high RR, high resistance on test lung, high compliance on test lung), while recording data.
* Simulate common failure modes (leaky loop, patient obstruction, etc), while recording data.
* Simulate patient inspiratory effort, record data.
* End test

*TODO(2020-04-29)* Clarify with Edwin: What behavior do we expect SW to have in extreme cases / failure modes?  Similarly, what behavior do we expect when simulating patient effort?  Current understanding is that, nothing is needed from software.

* Note: For patient effort, failure modes, and corner cases, we don't except the alpha software to do anything except continue to drive the respiration cycle according to the set parameters.  We just want to record what these cases look like to our sensors.

# Excluded

The alpha milestone is part of the project's overall [requirements](../../requirements). Anything mentioned there but not here, is excluded from alpha.

If you have further questions, ask on [#alpha-reqs](https://app.slack.com/client/T0102KRCH5M/C012H3G1GQ5/thread/C0100SF3N5T-1587858521.093800).

# Issue hotlists

Proceed with caution: these need cleanup.

- Controller: https://github.com/RespiraWorks/Ventilator/milestone/4
- GUI: https://github.com/RespiraWorks/Ventilator/milestone/1

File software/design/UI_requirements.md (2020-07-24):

# User Interface Requirements

The UI runs on a 1024x600 touchscreen. There are no external buttons or anything.

The UI requirements below come from several sources:
* Original mock-ups (the black-and-white mockups included
  [here](https://www.ics.com/blog/ics-joins-respiraworks-on-ventilator-project))
* [ICS prototype](http://demo.ics.com/ventilatorui-demo/) that was built based on the mock-ups
* [This paper](https://ccforum.biomedcentral.com/articles/10.1186/s13054-016-1431-1) and
  [this demo](https://www.youtube.com/watch?v=BT3snJ1Hm2s)
* [These notes](https://docs.google.com/document/d/1QFFcg2gL3PXXzyqgSBz3XZQm_oobZ2osFuErh492UEA/edit) from a
  conversation with a respiratory therapist

The list below is incomplete and possibly wrong in some ways.
Please consult Valispace and the main [Requirements page](../../requirements).
However, Valispace also does not have complete information at the time of writing. Proceed with caution.

## Self-test mode

On startup, ventilator is in self-test mode. It performs a set of checks and reports on the status.

Some checks are **automatic** _(eg that a certain tube is not blocked: turn on the blower, check that output flow
sensor detects some flow)_, Some are **manual** _(eg for "the buzzer works" it needs to turn on the buzzer and ask user
whether it's audible)_

The **full set of checks** is not yet known and generally open-ended.
Checks should include **guidance on how to fix** if it failed.
The self-test mode should be easy to use _(the hospital where the therapist above works decided not to purchase vents
where it was too cumbersome)_.
Results of self-test should be retained in memory.

**Open questions:**
* Should you be able to perform self-test only on startup or at any time?
* Should you confirm that patient is not connected?
* Should device refuse to operate if a check fails?

See also https://github.com/RespiraWorks/Ventilator/issues/307.

## Ventilation modes

We intend to support **Command Pressure** _(device commands all breaths)_, **Pressure Assist** _(device detects inhale
effort and helps that breath, but also initiates breaths if patient doesn't)_, **CPAP with O2 therapy aka HFNC** _(light
constant positive O2-saturated air pressure, non-invasive)_.

_Note: Different sources seem to indicate that pressure-controlled modes are going out of favor and volume control is
preferable (regular - not PRVC or VC+) - eg see
[notes](https://docs.google.com/document/d/1QFFcg2gL3PXXzyqgSBz3XZQm_oobZ2osFuErh492UEA/edit). But for v0.2 we're doing
pressure control._

**Mode parameters**: Each mode has several parameters defining it, e.g. Respiratory Rate, PIP (Peak Inspiratory
Pressure), PEEP (Positive End-Expiratory Pressure), FiO2 (O2 percentage). Parameter changes must be confirmed before
taking effect.

**Displayed measurements**: In each mode we display real-time graphs and sensor readings of several measured values:
pressure, flow, volume.

**Measured vs. commanded values**: All or almost all values have a "commanded" and "measured" value. E.g. ventilator
tries to achieve a certain PIP - this is the "commanded" value - but what it actually achieves is the "measured" value.
If they're too far off, this is bad and usually triggers an alarm.

## Alarms
**Alarm formats:**
* https://docs.google.com/document/d/1bMZfkq_p8dkg7F0ZGVIFhityv-s3GVRMsm_Nd1zNlww/edit#heading=h.yvoratpyj4xl
* Specifies visual flashing frequency / duty cycle
* Specifies auditory pulse frequency / pattern
* Derived from 60601-1-8

**Alarm conditions:**
The main alarm types for v0.2 are **"measured value too far from commanded value"** and **"the device is in a bad
state"** _(eg some tube disconnected, battery low etc)_.

Consider a **"check settings"** alarm. Per
[notes](https://docs.google.com/document/d/1QFFcg2gL3PXXzyqgSBz3XZQm_oobZ2osFuErh492UEA/edit) drs check settings every
3-6 hours, so maybe we should issue a low-prio alarm if settings haven't been confirmed in longer than that.

**Alarm presentation:**
* Alarms are indicated visually and sometimes audially (buzzer, continuous tone).
* A good way to display the "measured value off" alarm is to color the wrong value's background.
* At any moment the GUI must display the highest-priority alarm.
* You should be able to see all active alarms

**Alarm priorities:** low, medium, high (buzzer), and one or two alarms emit a continuous beep.

**Alarm lifecycle:**
* The alarm becomes active when its condition is met.
* Open question: We haven't figured out a general rule for when an alarm stops being active.
* Alarms can be suppressed in several ways: eg. cancel a particular alarm _(we don't know exactly what this means)_,
suspend all audial alarms for 2 minutes, etc. (see `01_Alarms` in Valispace)

**General advice:**
* Alarm fatigue is real. Need to make alarm management simple and conductive towards minimizing fatigue.

**Additional alarms per ISO 80601-2-12:**
(See [Slack thread](https://respiraworks.slack.com/archives/C011UMNUWGZ/p1591500042061800?thread_ts=1591207530.031400&cid=C011UMNUWGZ))


## Event logs (not in v0.2)

GUI must include a way to view the event log. It must include:
* All alarm-related events (activated, cancelled etc)
* Confirmed parameter changes and mode changes

## Non-functional requirements
The screen resolution is 1024x600.

**Remote observation/control**
* Things must be **visible from a distance of N meters**. The Covent reqs say from 1 meter, but per
[notes](https://docs.google.com/document/d/1QFFcg2gL3PXXzyqgSBz3XZQm_oobZ2osFuErh492UEA/edit) drs often want to observe
the screen from outside the patient's room, to decrease exposure to infection.
* Nice-to-have: remote control - also to decrease exposure.

**Usability:**
* Errors can kill a patient, and the UI is used by overworked staff. It is very important to design for minimizing
  chance of human error and minimizing dr fatigue.
* Staff in target markets where there's no vents will be inexperienced with vents. UI should help them, eg understand
  the numbers, guide towards configuring things right.
  * Example: in volume-controlled modes, there's an ideal volume of 4-8mL per kg of ideal body weight (based on
    gender/height). Could set default volume by that and color-code if setting outside this range.

Consider the likely working conditions - need a dark theme (optionally light theme too).

The UI should be colorblind-friendly, at least for elements where discerning the color is safety-critical.

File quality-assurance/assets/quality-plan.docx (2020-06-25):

Quality Plan

Daniel Burnham

# 1.0 Purpose

This document outlines the quality plan for the Respira Works ventilator system. It covers the development quality plan of the device which will be followed from concept phase, through design development, it does not cover the design transfer phase or manufacturing quality.

# 2.0 Definitions

1.0 Design Input – Safety, physical, and performance requirements of a device that are used as a basis for device design.
2.0 Design Review – evaluation of outputs to review completeness and accuracy of design.
3.0 Design Verification – Confirmation that design output specifications conform to design input requirements.
4.0 Design Validation – Confirmation that the device conforms with defined user needs and intended uses
5.0 Design History File (DHF) – compilation of records related to the design of a device.
6.0 Device Master Records (DMR) – records and specifications that define the procedure for production of a device.
7.0 Specification – Any requirement with which a product, process, service, or other activity must conform.
8.0 User Needs – Qualitative inputs that consider the needs of the user including usability, capability which inform indications for use of the device as well as inputs for design.

# 3.0 Project Phases

The ventilator development effort will be broken into several phases to ensure that inputs and development outputs are clearly defined at each phase and will be included in the design history file (DHF). These phases will be closed with a phase review prior to the conclusion of the proceeding phase. The deliverables in the previous phase can be revisited after the phase has been closed provided a proper regression analysis analyzing the impact of modifications is performed. These phases consist of:

- Design Planning and Definition Phase
- Design Development Phase
- Verification / Validation Phase
- Design Transfer

## 3.1 Design Planning and Definition Phase

This phase consists of developing a plan for the design of the device and defining the device inputs. The outputs of this phase is a development plan, user needs analysis, user risk analysis, and design inputs.

## 3.2 Design Development Phase

This phase consists of producing engineering outputs including subsystem requirements, engineering specifications (CAD drawings, circuit schematics, source code, etc..), and a design risk assessment.

## 3.3 Verification/Validation Phase

This phase includes defining verification / validation test methods and the performance of these test plans. The output of this phase is a verification and validation test report.

## 3.4 Deliverable Overview

Deliverable | Design Planning Phase | Design Development Phase | Design Verification/Validation Phase
Development/Quality Plan | Creation/Review
User Needs | Creation/Review
Design Inputs | Creation /Review | Update
System Risk Analysis | Hazard / Source Identification | Mitigation Development | Risk Control Analysis / Report
Design Specifications | | Creation/Review
Design Risk Assessment | | Creation/Review
Design Verification Plan / Report | | | Creation / Review
Design Validation Plan / Report | | | Creation / Review

# 4.0 Design History File (DHF)

The Design History File (DHF) shall contain or reference the records necessary to demonstrate that the design was developed in accordance with the quality plan. All phase deliverables, design reviews and other applicable design information shall be kept in the DHF. The quality lead is responsible for keeping accurate record of the DHF

Quality Plan

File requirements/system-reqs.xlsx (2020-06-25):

RespiraWorks Systems Requirements
Downloaded by | Ethan Chaleff
Downloaded on | May 27 2020, 11:52 am PT
Downloaded from | https://covent-19.valispace.com/specifications/groups/21/requirements
Not Reviewed or Released
Section | identifier | title | Requirement
1_General_Product | RW-SYS-016 | Reliability | The device must be able to work continuously (100% duty cycle) for a minimum of 48 hours and a target of 2 weeks without pause for maintenance, downtime, or repair.
1_General_Product | RW-SYS-057 | Power Requirements AC | The system shall be compatible with 110V/60Hz and 220V/50HZ AC mains.
1_General_Product | RW-SYS-074 | Power Requirements DC | The ventilator shall be capable of being run from a 12V power supply
1_General_Product | RW-SYS-024 | Compatible with standard/portable O2 and air supply line. | The device shall be compatible with oxygen (DISS) and supply line interfaces standards
1_General_Product | RW-SYS-063 | Hot water humidifier | The device shall be have the ability to integrate a hot water humidifier, the humidifiers that meet ISO 80601-2-74:2017 are compatible with 22mm Respiratory Tubing per ISO 5356 standard. (Note that the fitting for standard breathing tubes and humidifiers is the same)
1_General_Product | RW-SYS-076 | Max 02 Line Pressure | The system shall be compatible with O2 pressure lines up to 440Kpa
1_General_Product | RW-SYS-136 | Gas inlet markings | Gas inlet shall be clearly labelled with gas type, color, and specified pressure ranges along with direction of flow
1_General_Product | RW-SYS-135 | Shock and Vibration | The ventilator shall comply with shock and vibration tests as outlined in 80601-2-12
1_General_Product | RW-SYS-017 | Display | The device parameters and alarms shall be readable and/or audible at a distance of 1m
1_General_Product | RW-SYS-069 | Logging: Information Storage | The ventilator shall provide non-volatile data storage for at least 5000 events in an event log, including at least the following items: - Ventilation starts and stops - All confirmed Ventilation settings - All confirmed alarm settings - All occurrences and ends of alarms with all their related actions: Inhibitions, cancellations, resets, acknowledge button presses.The ventilator shall provide a date and time stamp for all event log data. The event log shall note any change to the system’s Real Time Clock by logging the Current Date/Time followed by the new Date/Time and a unique event code indicating the change.
1_General_Product | RW-SYS-054 | Human Safe Components | The system components that come into contact with the patient airway circuit shall be compatible with the following standards ISO 18562-1 First Edition 2017-03: Biocompatibility Evaluation of Breathing Gas Pathways in Healthcare Applications - Part 1: Evaluation and Testing Within a Risk Management Process ISO 18562-2 First Edition 2017-03: Biocompatibility Evaluation of Breathing Gas Pathways in Healthcare Applications - Part 2: Tests for Emissions of Particulate Matter ISO 18562-3 First Edition 2017: Biocompatibility Evaluation of Breathing Gas Pathways in Healthcare Applications - Part 3: Tests for Emissions of Volatile Organic Compounds ISO 18562-4 First Edition 2017-03: Biocompatibility Evaluation of Breathing Gas Pathways in Healthcare Applications - Part 4: Tests for Leachables in Condensate
1_General_Product | RW-SYS-137 | Altitude operation | Ventilator shall operate at altitudes below 10k ft
1_General_Product | RW-SYS-140 | Cleaning | The ventilator construction shall continue to operate while being disinfected by standard cleaning agents (e.g. bleach)
1_General_Product | HW-024 | Anti-Asphyxiation and Anti-Barotrauma | Patient needs to be protected against both asphyxiation and barotrauma in the event of a power, mechanical, or computing failure.
2_Ventilator_modes | RW-SYS-131 | Pretest Mode | The ventilator shall have a pre-test mode where the patient inhalation port and patient exhalation port are connected and the operation of the device is checked including the capability to produce the correct pressure and flow rate, the function of valves, and the function of tidal volume measurement.
2_Ventilator_modes | RW-SYS-132 | Pressure Assist Mode | The system shall support Pressure Assist Mode. In this mode a breath cycle is defined by the control parameters below. The patient can exceed the respiratory rate by initiating additional breaths, but the breath parameters do not change.Control parameters:PIP. Peak Inspiratory Pressure.PEEP. Positive End-Exhalatory Pressure.FiO2. Fraction of Inspired Oxygen.I-time. Inspiratory (rise + dwell) time.Inspiratory sensitivity.RR. Respiratory Rate.Display parameters: PIP/PEEP/RR/FiO2/I-time.Relevant Alarms: * Low tidal volume * High tidal volume * High RR
2_Ventilator_modes | RW-SYS-133 | Pressure Support Mode | The system shall support Pressure Support Mode. In this mode the breath cycle shall be defined by the control parameters below. The breath cycle shall be triggered exclusively by the patient.Control parameters:SIP: Support Inspiratory Pressure. Like PIP, but specified as a support pressure, not a target pressure.PEEP. Positive End-Exhalatory Pressure.FiO2. Fraction of Inspired Oxygen.I-time. Inspiratory (rise + dwell) time.Inspiratory sensitivityDisplay parameters: PIP/PEEP/RR/FiO2/I-time.Relevant Alarms: * Low tidal volume * High tidal volume * Low RR (apnea) *
2_Ventilator_modes | RW-SYS-134 | Pressure Control Mode | The system shall support Pressure Control Mode. This mode shall not be featured. It is effectively a subset of Pressure Assist with zero patient inspiratory effort.
2_Ventilator_modes | RW-SYS-077 | CPAP Pressure Support mode | The system shall support a HFNC operational mode. In this mode there are no breath cycles. The operator defines the following control parameters:* constant patient pressure (2-20 cmH2O, 2cm increments)constant pressure (2-20 cmH2O)constant flow rate (up to maximum possible L/min)constant FiO2 (21-100%).Needs a child requirement: Shall interface with nasal cannulas or pillows through a standard ET tube adapter interface.
3_Control_Parameters | RW-SYS-005 | Positive End-Expiratory Pressure (PEEP) control | The device shall allow the user to establish a PEEP from 0 - 20 cm H2O with increments of 2 cm H20.
3_Control_Parameters | RW-SYS-020 | Respiratory Rate control | The device shall be able to provide a Respiratory Rate between 5 - 30 BPM with increments of 1BPM. This is available in Pressure Assist Mode (RW-SYS-132)
3_Control_Parameters | RW-SYS-021 | I/E ratio control | The device shall be able to adjust the time ratio of inspiration and expiration from 1:1 to 1:4 (Inhale to exhale). Increments of 1: .1
3_Control_Parameters | RW-SYS-032 | Tidal Volume (TV) control | The device shall be able to support tidal volumes ranging from 200-800ml with increments of 10mL
3_Control_Parameters | RW-SYS-072 | Fraction of Infused Oxygen (FI02) control | The device shall be able to adjust the fraction of inspired O2 (FiO2) in supplied air from 0.21 to as close to 1 as possible with a minimum of 0.9, adjustable in increments of 0.05.
3_Control_Parameters | RW-SYS-078 | Minimum Respiratory Rate | The system shall allow the operator to set the minimum respiratory rate of the patient. The device shall initiate a breath If respiration falls below this rate. This control is available in A/C modes.
3_Control_Parameters | RW-SYS-079 | High Tidal Volume Level Alarm Trigger | This parameter will enable the operator to set a maximum inspiration tidal volume threshold between the bounds of 80 to 3000 ml in increments of 10ml
3_Control_Parameters | RW-SYS-080 | High Pip Alarm Trigger | This parameter will enable the operator to set a PIP maximum threshold. A High priority alarm will occur if the PIP level is above the HIGH PIP level for three consecutive breaths. For pressure assisted modes the high PIP shall be automatically set to PIP +5 cmH20
3_Control_Parameters | RW-SYS-081 | High Leak Level Alarm Trigger | This parameter will enable the operator to set a maximum leak threshold between the bounds of 5 to 150 lpm.
3_Control_Parameters | RW-SYS-127 | Low Tidal Volume Alarm Trigger | This parameter will allow the operator to set a minimum inspiration tidal volume threshold between the bounds of
3_Control_Parameters | RW-SYS-128 | High Respiratory Rate Alarm Trigger | This parameter will allow the operator to set a maximum respiratory rate between the bounds of 5-30 in increments of 1 BPM
3_Control_Parameters | RW-SYS-130 | Apnea Alarm Trigger | This parameter will allow the operator to set an apnea alarm trigger between the range of 1-30s with 1s incremements.
3_Control_Parameters | RW-SYS-003 | Peak Inspiratory Pressure (PIP) | The device must be capable of supplying an inspiratory pressure from 5-55 cmH2O with increments of 1 cm H2O.
3_Control_Parameters | RW-SYS-129 |  | This parameter will allow the operator to set a minimum respiratory rate between the bounds of 2-30 in increments of 1 BPM
4_Performance_Requirements | RW-SYS-083 | Patient Pressure measurement | The ventilator shall display the current patient pressure measured at the gas outlet port. The system shall display this information as a graph with duration of 30 seconds updated at a rate > 25 Hz
4_Performance_Requirements | RW-SYS-084 | Tidal Volume measurement | The system shall display the inspiratory tidal volume in range of 0mL to 3000mL with resolution of 1mL
4_Performance_Requirements | RW-SYS-085 | I:E ratio measurement | The system shall display the ratio of the inspiration time to the expiration time in the range of 10:1 to 1:200 with display resolution of 0.1 for values under 10 and 1 for values over 10.
4_Performance_Requirements | RW-SYS-086 | PEEP measurement | The system shall measure and display the PEEP in increments of 1 cmH2O
4_Performance_Requirements | RW-SYS-087 | Instantaneous Volume Measurement | The system shall display the flow rate provided to the patient as a graph with duration of 30 seconds updated at a rate &gt;25Hz and units of liters / minute.
4_Performance_Requirements | RW-SYS-042 | Assist Control Mode Delay | During patient assist control modes, the device shall provide patient pressure within 100 ms after onset of respiratory effort (Ppat < PEEP) Pressure assist mode/ Pressure support and others
4_Performance_Requirements | RW-SYS-045 | Tidal Volume per minute | The device shall be cable of delivering a minute volume of 30 liters / minute.
4_Performance_Requirements | RW-SYS-088 | General Performance Requirements | Commanded parameters not specified in the requirements shall be within 10% of the commanded value
4_Performance_Requirements | RW-SYS-089 | Inspiration Trigger Performance | Inspiration cycle shall be triggered when XX (FLOW VS PRESSURE TRIGGER)
4_Performance_Requirements | RW-SYS-092 | Peak Inspiratory Flow Rate | The device shall be capable of a peak inspiratory flow rate of at least 80L/min (best case 120 L/min)
4_Performance_Requirements | RW-SYS-093 | Breath Rate | The output breath rate shall be within +-1 breath of the commanded value
4_Performance_Requirements | RW-SYS-094 | PEEP Pressure during the exhalation Pressure Fall | The pressure overshoot during the pressure fall phase shall not exceed 0.8*PEEP-1 cmH2O
4_Performance_Requirements | RW-SYS-095 | PEEP Pressure during the Exhalation Steady Phase | Actual PEEP shall be within PEEP setting +-1 cm H2O + 10%.
4_Performance_Requirements | RW-SYS-096 | Measured Respiratory Rate | The system shall measure the respiratory rate with an accuracy of +- 1 BPM
4_Performance_Requirements | RW-SYS-082 | Respiration Rate measurement | The ventilator shall compute and display the breath rate in increments of 1 breath/min.
4_Performance_Requirements | RW-SYS-050 |  | The device shall be capable of 4 hours (1.5 hours) [WHICH IS IT?] of battery powered operation at nominal settings.
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

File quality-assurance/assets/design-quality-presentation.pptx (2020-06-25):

## Design Quality Process

## Guiding Standards

- ISO 13485 - Medical devices -- Quality management systems
  - Standards that guides the development of medical devices
  - Voluntary Standard
  - Covers Organization, Human resources, Quality documentation system, design/development, manufacturing, parts sourcing…
- We are focusing on complying with design and development so that the design is well documented.
- This will allow us to quickly transition the design to a manufacturing partner and adhere to regulatory standards.
- The manufacturing partner or marketing partner is ultimately responsible for quality

## Project Phases

- Planning
  - Design Development/Quality Plan – defines how the project will be performed and what deliverables there will be in each phase
  - User Needs / Design Inputs – What do we want the product to do
  - Preliminary Risk Analysis
- Design Development
  - Where the design takes place
  - Deliverables are subsystem requirements (software, electrical)
  - Design Risk Analysis (DFMEA)
  - Design Outputs – Specifications (CAD, schematic, source code and design reviews)
- Verification
  - Activities showing that requirements were met and works as intended. Includes protocols with established criterion
- Validation
  - Activities which show that user needs were met. Addresses clinical use.
- Design Transfer – The transfer to manufacturing (will be handled later)

## Documentation

- The records of the design go into a Design History File (DHF)
- These documents will be kept in a separate location from the general development files
  - Approved Requirements
  - Risk Analysis
  - Final Design Outputs
  - Verification Protocols and Reports
- Phase Reviews
  - At the end of each phase there will be a phase review which shows that all deliverables were met.

## Software Quality

- IEC 62304 Provides a guideline on the software development lifecycle
- Requires Established Lifecycle Plan with the following
  - Software Architecture – High level description
  - Software Detailed Design – Unit/Module level documentation
  - Software Development Environment definition – IDE/compiler etc..
  - Software Risk Analysis
  - Software Requirements
  - Software Unit Testing
  - Software Integration Testing
  - Software Validation

## Our Approach

- Initial prototype development can continue without all processes in place.
- We should do enough to ensure that the design is safe and controlled
  - Risk Analysis should be complete and design outputs should be frozen
  - Verification should be done to ensure that there are no issues.
- As we near the need for the next phase we can evaluate and determine what documentation we need to close out the current phase. Quality people will make sure that documentation is transferred to a controlled location and labelled.
- The compliance is ultimately up to the company marketing the product.
- Regulatory requirements vary country to country and are also relaxed in time of emergency.

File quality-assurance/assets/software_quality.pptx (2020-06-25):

## Software Quality for Medical Devices

## 62304 Overview

- IEC 62304 – International Medical device software lifecycle standard
- Mandates that the developing entity have the following:
  - Software quality standards
  - Software risk analysis
  - Defined software development process
  - Software architecture and detailed design definition
  - Software release configuration management
  - Software testing structure
  - Software maintenance plan

## Deliverables from 62304

- Determined by software risk class

Software documentation | Class A | Class B | Class C
Software development planning | X | X | X
Software requirements analysis | X | X | X
Software architectural design | | X | X
Software detailed design | | | X
Software unit implementation | X | X | X
Software unit verification | | X | X
Software integration and integration testing | | X | X
Software system testing | | X | X
Software release | X | X | X

## Software Classification

- Controller Software is definitely a Class C software
- Depending on what we end up architecting UI may be class B, but probably better to approach as class C for now

## Software development plan

- Defines the following
  - Requirements Management
  - Lifecycle model – Agile/waterfall or combination
  - Development Environment
    - Tools – Languages Toolchain, Test automation tools, IDE etc..
    - Configuration Management– git, CI
    - Coding standards
    - Any libraries that are necessary
  - Bug/Issue reporting process
  - Plans for handling software not developed internally (SOUP) – QT etc..

## Software Requirements Documentation

- Separate from system requirements
- Need to be broken down into:
- Types
  - Non-Functional – Hardware requirements, constraints, etc..
  - Functional – What the software will do
  - Performance – Specific performance requirement
    - (Software shall Perform XX in XX with XX accuracy)
- Areas
  - States of the software
  - Module functional specifications
  - Usability /UI specifications
  - Interface Specifications – To hardware, other software etc..

## Software Risk Analysis

- Go through hazards that can be caused by the software
  - Hazard to patient
  - Hazard to clinician
  - Cybersecurity
- Two approaches
  - Top Down – Start with hazards defined in the system hazards, and say how software can contribute (Fault Tree)
  - Bottom up – Analyze each module and state how this can lead to failure (DFMEA, single fault)
  - Combine both into single Analysis

## Software Architecture

- High level description of the software before implemented
- Physical Description
  - Controller Software runs on controller board
  - UI runs on Raspberry PI
  - Connected by UART
- Block Diagram of software modules
  - Include the SOUP (QT, RTOS etc..)
- Software Interfaces
- Workflow or desired states
- Trace from the architecture to the requirements

## Software Detailed Design

- Documentation stating how it will be done (can be iterative in agile approach)
- Detailed documentation
  - UML charts
  - Functional descriptions
  - Algorithm overview
- Trace from the detailed design to the requirements
  - Ex. Module XX implements XX requirement

## Verification

- Unit Testing
  - Plan with acceptance criteria – Document what the unit test is testing and what the expected outputs are
  - Test variable init, boundary conditions, memory management as needed
- Integration Testing
  - Integration Test Plan – Have plan for how we will integrate the components and test together
- System Verification
  - Verify that all requirements are met and that all risk mitigations work

## Software Maintenance

- Let’s decide this later
  - Who we partner with and how we distribute will affect this.
  - At minimum we will have to track bugs and talk about how these get triaged.

## How we can Implement?

- TBD – We need to come to a consensus on how to manage
- Group called Innolitics developed RDM to simplify process in github. Takes yaml and creates markdown and PDF documents
  - https://github.com/innolitics/rdm
- My Recommendations
  - Keep as much documentation as we can in the github
    - Coding Standards, Toolchain definitions, tools, dependencies can be markdown pages
    - Architecture Can be implemented as a wiki or use RDM above
    - Software Requirements should be documented separately and referenced in all git issues. Tasks that aren’t related to software requirements specifically can be tagged with #devops, #bugfix etc..
    - Detailed Design – Tricky, usually defined a separate document, if we are disciplined, we could break software up into “module” folders and place documents defining each
    - Hazard analysis – Manage in excel similar to the systems hazard analysis
    - Verification – Will need to define the protocols and reports
      - Unit Testing – Can use generator in the comments of the unit test to generate all the documentation or potentially use issues (have done this in JIRA)
- As long as we have all this and follow the process we can reformat the documents later for submission.

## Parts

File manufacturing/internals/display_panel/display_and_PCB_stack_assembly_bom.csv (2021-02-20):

Item | Part Number | QTY | Title | Estimated Cost | REV | Manufacturer | Vendor | Vendor Part Number | Optional | Comments | Keywords
1 | ELEV03EA0001 | 1 | Touchscreen | $49.00 | V0.3 | UPerfect | [AliExpress](https://www.aliexpress.com/item/4000747984746.html) | 4000747984746 | No | 7" capacitive touchscreen with speakers | electrical, sourced, internals, display_assembly
2 | ELEV03RW0002 | 1 | Open CASCADE Shape Model of the PCB |  | v0.3 | RespiraWorks | [RespiraWorks](https://github.com/RespiraWorks/Ventilator/blob/issue_1011_automated_bom/pcb) |  | No | RespiraWorks custom PCB | electrical, custom, internals, display_assembly
3 | ELEV03EM0002 | 1 | Nucleo board | $14.43 | v0.3 | ST Micro | [Mouser](https://www.mouser.com/ProductDetail/STMicroelectronics/NUCLEO-L452RE [RSComputing](https://export.rsdelivers.com/product/stmicroelectronics/nucleo-l452re/stmicroelectronics-stm32-nucleo-64-mcu/1261775) | 511-NUCLEO-L452RE | No | STM32 Nucleo dev board, DO NOT get the -P version | electrical, sourced, internals, display_assembly
4 | ELEV03EM0003 | 1 | Raspberry Pi Board | $52.23 | v0.3 | Raspberry Pi | [Mouser](https://www.mouser.com/ProductDetail/Raspberry-Pi/RPI4-MODBP-2GB-BULK | RPI4-MODBP-2GB | No | Raspberry Pi 4 | electrical, sourced, internals, display_assembly
5 | ELEV03RW0004 | 1 | Interim Board |  | v0.3 | RespiraWorks | [RespiraWorks](https://github.com/inceptionev/VentilatorRev1InterimDaughtercard) |  | Yes | RespiraWorks Rev1 interim board | electrical, custom, internals, display_assembly
6 | MECV03EM0001 | 4 | PCB Lower Standoff | $0.59 | v0.3 | Wurst Elektronik | [Digikey](https://www.digikey.com/en/products/detail/w-rth-elektronik/971090151/6174614) | 732-10395-ND | No | M2.5 standoff, 9mm tall | mechanical, sourced, internals, display_assembly
7 | MECV03EM0002 | 4 | RaspberryPi Upper Standoff | $0.62 | v0.3 | Wurst Elektronik | [Digikey](https://www.digikey.com/en/products/detail/w%C3%BCrth-elektronik/971200151/6174654) | 732-10435-ND | No | M2.5 standoff, 20mm tall | mechanical, sourced, internals, display_assembly
8 | ELEV03ED0005 | 2 | Stepper Driver Board | $10.64 | v0.3 | RespiraWorks | [Digikey](https://www.digikey.com/short/z442qt) [Mouser](https://www.mouser.com/ProductDetail/511-X-NUCLEO-IHM03A1) | X-NUCLEO-IHM03A1 | No | One-axis stepper driver board | electrical, sourced, internals, display_assembly
9 | MECV03EM0003 | 4 | Touchscreen Mounting Locknut | $7.70 | v0.3 | McMaster-Carr | [McMaster-Carr](https://www.mcmaster.com/93625A101/) | 93625A101 | No | M2 lock nut | mechanical, sourced, internals, display_assembly
10 | MECV03EM0004 | 4 | Touchscreen Mounting Washer Front | $1.06 | v0.3 | McMaster-Carr | [McMaster-Carr](https://www.mcmaster.com/93475A195/) | 93475A195 | No | M2 washer, 5mm OD | mechanical, sourced, internals, display_assembly
11 | MECV03EM0005 | 4 | RasberryPi Mounting Screw | $0.05 | v0.3 | McMaster-Carr | [McMaster-Carr](https://www.mcmaster.com/92095A458/) | 92095A458 | No | M2.5 screw, 6mm | mechanical, sourced, internals, display_assembly
12 | MECV03EM0006 | 4 | Touchscreen Mounting Screw | $7.44 | v0.3 | McMaster-Carr | [McMaster-Carr](https://www.mcmaster.com/92095A455/) | 92095A455 | No | M2 screw, 12mm | mechanical, sourced, internals, display_assembly
13 | MECV03EM0007 | 4 | Touchscreen Mounting Washer Back | $2.40 | v0.3 | McMaster-Carr | [McMaster-Carr](https://www.mcmaster.com/91116A240/) | 91116A240 | No | M2 washer, 7mm OD | mechanical, sourced, internals, display_assembly
14 | ELEV03EX9001 | 1 | Alternate Stepper Driver Board | $15.00 | v0.3 | ST Micro | [ST](https://www.st.com/en/ecosystems/x-nucleo-ihm02a1.html#sample-and-buy) [RSComputing](https://export.rsdelivers.com/product/stmicroelectronics/x-nucleo-ihm02a1/stmicroelectronics-x-nucleo-ihm02a1-two-axis/1646982) | X-NUCLEO-IHM02A1 | Yes | Two-axis stepper driver board, Alternative to 2x ELEV03ED0005 | electrical, sourced, internals, display_assembly, alternate

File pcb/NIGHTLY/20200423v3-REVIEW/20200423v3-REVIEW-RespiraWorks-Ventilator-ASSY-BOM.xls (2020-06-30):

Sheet: BOM Report
 |  | Bill of Materials
Source Data From: |  | RespiraWorks Ventilator.PrjPcb
Project: |  | RespiraWorks Ventilator.PrjPcb
Variant: |  | None
Creation Date: | 4/23/2020 | 10:51:32 PM
Print Date: | 2020-04-23 | 43944.9532
Line no. | Designator | Description | Value | PCB Package | Manufacturer | Manufacturer P/N | Do Not Populate | Quantity
1 | C1, C22, C24, C26, C28, C29, C30, C31, C32, C35 | Cap 0603 | 0.1uF | 0603 | Yageo | CC0603KRX7R7BB104 |  | 10
2 | C2, C10, C14, C18, C23, C27, C33, C34, C36 | Cap 0603 | 1uF | 0603 | Yageo | CC0603KRX7R6BB105 |  | 9
3 | C3, C25 | Cap 0603 | 0.1uF | 0603 | Yageo | CC0603KRX7R8BB104 |  | 2
4 | C4, C21, C37 | Cap 1210 | 10uF | 1210 | Murata | GRM32DR71E106KA12L |  | 3
5 | C5 | Cap 1210 | 47uF | 1210 | Murata | GRM32ER71A476KE15L |  | 1
6 | C6 | Cap 0603 | 47pF | 0603 | Kemet | C0603C470J1GACTU |  | 1
7 | C7 | Cap 0603 | 750pF | 0603 | Samsung | CL10B751KB8NNNC |  | 1
8 | C8, C12, C16 | Cap 0603 | 470pF | 0603 | Yageo | CC0603MRX7R9BB471 |  | 3
9 | C9, C13, C17 | Cap 0603 | 1.5uF | 0603 | TDK | C1608X7R1A155K080AC |  | 3
10 | C11, C15, C19, C38, C39 | Cap 0603 | 0.01uF | 0603 | Samsung | CL10B103KO8NNNC |  | 5
11 | C20 | Cap 0603 | 0.22uF | 0603 | Yageo | CAP CER 0.22UF 10V X7R 0603 |  | 1
12 | D1 | TVS Diode, Zener, 15V Standoff, 24V Clamp, 8.2A |  | SOD-123F | Littelfuse | SMF15A |  | 1
13 | D3 | DIODE SCHOTTKY 60V 3A SMA |  | DO-214AC (SMA) | Diodes Inc. | B360AM-13-F |  | 1
14 | D4 | LED 0603 | Green | 0603 | Lite-On | LTST-C191KGKT |  | 1
15 | D5, D6 | Ultra-Fast Signal Diode, Silicon, 100V, 300mA |  | DO-214AB, SMC | Diodes Inc. | S8MC-13 |  | 2
16 | D7, D10 | LED 3528 GREEN 500mcd | Green | 2-LED3528 | Kingbright | AA3528ZGSK |  | 2
17 | D8, D11 | LED 3528 RED 450mcd | Red | 2-LED3528 | Kingbright | AA3528SESK/J3 |  | 2
18 | D9, D12 | LED 3528 YELLOW 450mcd | Yellow | 2-LED3528 | Kingbright | AA3528SYCKT/J3 |  | 2
19 | F1 | Fast Blow Nano Fuse in Holder, 10A, 125V | 10A (hold) |  | Littelfuse | 0154010.DR |  | 1
20 | F2, F3 | PTC Fuse, 2A Hold, 24V, 2920 size |  | 2920 | Belfuse | 0ZCF0200AF2C |  | 2
21 | J1 | BARREL 5.5x2.1 POWER JACK, 5A |  | PJ-102AH | CUI | PJ-102AH |  | 1
22 | J2, J6, J7, J8 | CONN HEADER PH TOP 5POS 2MM |  |  | JST Sales America Inc. | B5B-PH-K-S(LF)(SN) |  | 4
23 | J3 | CONN HEADER PH TOP 2POS 2MM |  |  | JST Sales America Inc. | B2B-PH-K-S(LF)(SN) |  | 1
24 | J4 | 10 _8 + 2_ Position Card Connector microSD Surface Mount, Right Angle Gold |  |  | Molex | 5031821852 |  | 1
25 | J5 | CONN HEADER PH TOP 6POS 2MM |  |  | JST Sales America Inc. | B6B-PH-K-S(LF)(SN) |  | 1
26 | J9 | CONN HEADER PH TOP 3POS 2MM |  |  | JST Sales America Inc. | B3B-PH-K-S(LF)(SN) |  | 1
27 | J10 | JST-VH HEADER VERT 2POS 3.96MM |  |  | JST | B2P-VH(LF)(SN) |  | 1
28 | L1 | Inductor, 501 Series, Shielded 2.2uH, 4A | 3.3uH | SRP5015 | Bourns | SRP5015TA-3R3M |  | 1
29 | P1 | Tall Female Header 0.100" Pitch 20x2 Sockets |  | ESQ-120-44-L-D | Samtec | ESQ-120-44-L-D |  | 1
30 | P2, P3 | Female Header, 0.100" Pitch, 19x2 |  |  | Sullins | PPPC192LFBN-RC |  | 2
31 | Q1, Q4, Q5, Q6, Q7, Q8, Q9 | Transistor, BJT NPN, General Purpose 40V |  | SOT23 | Fairchild | MMBT3904 |  | 7
32 | Q2, Q3 | Transistor, BJT NPN, General Purpose 40V |  | 8-SOIC | On Semi | FDS4672A |  | 2
33 | R1, R66 | Res 0603 | 0 | 0603 | Yageo | RC0603JR-070RL |  | 2
34 | R2, R67 | Res 0603 | 0 | 0603 | Yageo | RC0603JR-070RL | DNP | 2
35 | R3, R4, R19, R20, R21, R22, R26, R27, R28, R32, R33, R34, R50, R52, R54, R55 | Res 0603 | 1k | 0603 | Yageo | RC0603FR-071KL |  | 16
36 | R5 | Res 0603 | 64.9k | 0603 | Yageo | RC0603FR-0764K9L |  | 1
37 | R6 | Res 0603 | 60.4k | 0603 | Yageo | RC0603FR-0760K4L |  | 1
38 | R7 | Res 0603 | 150 | 0603 | Panasonic | ERJ-3EKF1500V |  | 1
39 | R8, R61, R62, R63, R64, R65, R70, R71 | Res 0603 | 10k | 0603 | Panasonic | ERJ-3EKF1002V |  | 8
40 | R9 | Res 0603 | 76.8k | 0603 | Yageo | RC0603FR-0776K8L |  | 1
41 | R10 | Res 0603 | 11.5k | 0603 | Yageo | RC0603FR-0711K5L |  | 1
42 | R11 | Res 0603 | 24k | 0603 | Panasonic | ERJ-3EKF2402V |  | 1
43 | R12, R13, R14 | Res 0603 | 1.5k | 0603 | Yageo | RC0603FR-071K5L |  | 3
44 | R15 | Res 0603 | 35.7k | 0603 | Yageo | RC0603FR-0735K7L |  | 1
45 | R16, R51, R53 | Res 0603 | 10k | 0603 | Yageo | RC0603FR-0710KL |  | 3
46 | R17, R18 | Res 0603 | 4.7k | 0603 | Yageo | RC0603FR-074K7L | DNP | 2
47 | R23, R29 | Res 0603 | 84.5 | 0603 | Yageo | RC0603FR-0784R5L |  | 2
48 | R24, R30 | Res 0603 | 140 | 0603 | Yageo | RC0603FR-07140RL |  | 2
49 | R25, R31 | Res 0603 | 150 | 0603 | Yageo | RC0603FR-07150RL |  | 2
50 | R35, R36, R37, R38, R39, R40, R41, R42, R43, R44, R45, R46, R47, R48, R49 | Res 0603 | 4.7k | 0603 | Yageo | RC0603FR-074K7L |  | 15
51 | R56, R57, R58 | Res 0603 | 3k | 0603 | Yageo | RC0603FR-073KL |  | 3
52 | R59, R60, R68, R69 | Res 0603 | 10k | 0603 | Panasonic | ERJ-3EKF1002V | DNP | 4
53 | S1 | Buzzers Transducer, Externally Driven Magnetic 5V 60mA 2.4kHz 88dB @ 5V, 10cm Surface Mount Solder Pads | 88dbA | CT-1205H-SMT-TR | CUI | CT-1205H-SMT-TR |  | 1
54 | TP1, TP2, TP3, TP4, TP5, TP6, TP7, TP8, TP9, TP10, TP11, TP12, TP13 | Keystone 5015 SMT Mini Testpoint |  | TP-5015 | Keystone | 5015 |  | 13
55 | U1 | STM32F446RE Nucleo MCU Board |  |  | ST | NUCLEO-L452RE | DNP | 1
56 | U2 | DC-DC Buck, 60V Input, 3.5A Int Sw, Ultra Low Quiescent Power |  | SOIC8 | Texas Instruments | TPS54360DDAR |  | 1
57 | U3, U4, U5 | Pressure Sensor 0.57PSI (3.92kPa) Differential Male - 0.13" (3.3mm) Tube, Dual 1 V ~ 4.9 V 8-BSOP (0.475", 12.06mm Width) Dual Ports, Same Side |  | 8-SOP-MPXV | NXP | MPXV5004DP |  | 3
58 | U6 | Watchdog Timer Circuit, 1.6s timeout |  | SOT-23-5 | ST | STWD100NYWY3F |  | 1
59 | U8 | Raspberry Pi B+ Footprint direct on PCB |  |  | Raspberry Pi | B+ | DNP | 1
60 | U9 | IC I2C SW 4CH W/RESET 20TSSOP |  | 20-TSSOP | Texas Instruments | TCA9544APWR |  | 1
 |  |  |  |  |  |  |  | 169

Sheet: Project Information
Project Full Path | C:\Projects\pcbreathe\RespiraWorks Ventilator.PrjPcb
Project Filename | RespiraWorks Ventilator.PrjPcb
Variant Name | None
Data-Source Filename | RespiraWorks Ventilator.PrjPcb
Data-Source Full Path | C:\Projects\pcbreathe\RespiraWorks Ventilator.PrjPcb
Title | RespiraWorks
Total Quantity | 169
Report Time | 10:51:32 PM
Report Date | 4/23/2020
Report Date & Tine | 4/23/2020 10:51:32 PM
Output Name | Bill of Materials
Output Type | BOM_PartType
Output Generator Name | BOM
Output Generator Description | Bill of Materials

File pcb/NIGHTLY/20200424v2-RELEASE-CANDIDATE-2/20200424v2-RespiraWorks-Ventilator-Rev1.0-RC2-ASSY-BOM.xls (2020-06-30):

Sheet: BOM Report
 |  | Bill of Materials
Source Data From: |  | RespiraWorks Ventilator.PrjPcb
Project: |  | RespiraWorks Ventilator.PrjPcb
Variant: |  | None
Creation Date: | 4/25/2020 | 12:33:36 AM
Print Date: | 2020-04-25 | 43946.0237
 | Designator | Description | Value | PCB Package | Manufacturer | Manufacturer P/N | Do Not Populate | Quantity
 | C1, C22, C24, C26, C28, C29, C30, C31, C32, C35 | Cap 0603 | 0.1uF | 0603 | Yageo | CC0603KRX7R7BB104 |  | 10
 | C2, C10, C14, C18, C23, C27, C33, C34, C36 | Cap 0603 | 1uF | 0603 | Yageo | CC0603KRX7R6BB105 |  | 9
 | C3, C25 | Cap 0603 | 0.1uF | 0603 | Yageo | CC0603KRX7R8BB104 |  | 2
 | C4, C21, C37 | Cap 1210 | 10uF | 1210 | Murata | GRM32DR71E106KA12L |  | 3
 | C5 | Cap 1210 | 47uF | 1210 | Murata | GRM32ER71A476KE15L |  | 1
 | C6 | Cap 0603 | 47pF | 0603 | Kemet | C0603C470J1GACTU |  | 1
 | C7 | Cap 0603 | 750pF | 0603 | Samsung | CL10B751KB8NNNC |  | 1
 | C8, C12, C16 | Cap 0603 | 470pF | 0603 | Yageo | CC0603MRX7R9BB471 |  | 3
 | C9, C13, C17 | Cap 0603 | 1.5uF | 0603 | TDK | C1608X7R1A155K080AC |  | 3
 | C11, C15, C19, C38, C39, C40 | Cap 0603 | 0.01uF | 0603 | Samsung | CL10B103KO8NNNC |  | 6
 | C20 | Cap 0603 | 0.22uF | 0603 | Yageo | CAP CER 0.22UF 10V X7R 0603 |  | 1
 | D1 | TVS Diode, Zener, 15V Standoff, 24V Clamp, 8.2A |  | SOD-123F | Littelfuse | SMF15A |  | 1
 | D3 | DIODE SCHOTTKY 60V 3A SMA |  | DO-214AC (SMA) | Diodes Inc. | B360AM-13-F |  | 1
 | D4 | LED 0603 | Green | 0603 | Lite-On | LTST-C191KGKT |  | 1
 | D5, D6 | Ultra-Fast Signal Diode, Silicon, 100V, 300mA |  | DO-221AC, SMA Flat Leads | Vishay | SE30AFG-M3/6A |  | 2
 | D7, D10 | LED 3528 GREEN 500mcd | Green | 2-LED3528 | Kingbright | AA3528ZGSK | DNP | 2
 | D8, D11 | LED 3528 RED 450mcd | Red | 2-LED3528 | Kingbright | AA3528SESK/J3 | DNP | 2
 | D9, D12 | LED 3528 YELLOW 450mcd | Yellow | 2-LED3528 | Kingbright | AA3528SYCKT/J3 | DNP | 2
 | F1 | Fast Blow Nano Fuse in Holder, 10A, 125V | 10A (hold) |  | Littelfuse | 0154010.DR |  | 1
 | F2, F3 | PTC Fuse, 2A Hold, 24V, 2920 size |  | 2920 | Belfuse | 0ZCF0200AF2C |  | 2
 | J1 | JST-VH HEADER VERT 3POS 3.96MM |  |  | JST | B3P-VH(LF)(SN) |  | 1
 | J2, J6, J7, J8 | CONN HEADER PH TOP 5POS 2MM |  |  | JST Sales America Inc. | B5B-PH-K-S(LF)(SN) |  | 4
 | J3 | CONN HEADER PH TOP 2POS 2MM |  |  | JST Sales America Inc. | B2B-PH-K-S(LF)(SN) |  | 1
 | J4 | 10 _8 + 2_ Position Card Connector microSD Surface Mount, Right Angle Gold |  |  | Molex | 5031821852 |  | 1
 | J5 | CONN HEADER PH TOP 6POS 2MM |  |  | JST Sales America Inc. | B6B-PH-K-S(LF)(SN) |  | 1
 | J9 | CONN HEADER PH TOP 3POS 2MM |  |  | JST Sales America Inc. | B3B-PH-K-S(LF)(SN) |  | 1
 | J10 | JST-VH HEADER VERT 2POS 3.96MM |  |  | JST | B2P-VH(LF)(SN) |  | 1
 | L1 | Inductor, 501 Series, Shielded 2.2uH, 4A | 3.3uH | SRP5015 | Bourns | SRP5015TA-3R3M |  | 1
 | M1, M2, M3, M4 | [BOM Item] Generic Standoff | M2.5 x 20mm + 4mm |  | Keystone | 24335 | DNP | 4
 | M5, M6, M7, M8, M17, M18, M19, M20 | [BOM Item] Generic Nut | M2.5 x 4mm |  | Keystone | 29300 | DNP | 8
 | M9, M10, M11, M12 | [BOM Item] Generic Nut | M3 x 6mm |  | Keystone | 29311 | DNP | 4
 | M13, M14, M15, M16 | [BOM Item] Generic Standoff | M2.5 x 20mm + 6mm |  | Wurth | 971090151 | DNP | 4
 | M21, M22, M23, M24 | [BOM Item] Generic Nut | M2.5 |  | Keystone | 4707 | DNP | 4
 | P1 | Tall Female Header 0.100" Pitch 20x2 Sockets |  | ESQ-120-44-L-D | Samtec | ESQ-120-44-L-D |  | 1
 | P2, P3 | Female Header, 0.100" Pitch, 19x2 |  |  | Sullins | PPPC192LFBN-RC |  | 2
 | Q1, Q4, Q5, Q6, Q7, Q8, Q9 | Transistor, BJT NPN, General Purpose 40V |  | SOT23 | Fairchild | MMBT3904 |  | 7
 | Q2, Q3 | Transistor, BJT NPN, General Purpose 40V |  | 8-SOIC | On Semi | FDS4672A |  | 2
 | R1, R66, R72, R74, R76 | Res 0603 | 0 | 0603 | Yageo | RC0603JR-070RL |  | 5
 | R2, R67, R73, R75, R77 | Res 0603 | 0 | 0603 | Yageo | RC0603JR-070RL | DNP | 5
 | R3, R4, R19, R20, R21, R22, R26, R27, R28, R32, R33, R34, R50, R52, R54, R55 | Res 0603 | 1k | 0603 | Yageo | RC0603FR-071KL |  | 16
 | R5 | Res 0603 | 64.9k | 0603 | Yageo | RC0603FR-0764K9L |  | 1
 | R6 | Res 0603 | 60.4k | 0603 | Yageo | RC0603FR-0760K4L |  | 1
 | R7 | Res 0603 | 150 | 0603 | Panasonic | ERJ-3EKF1500V |  | 1
 | R8, R61, R62, R63, R64, R65, R70, R71 | Res 0603 | 10k | 0603 | Panasonic | ERJ-3EKF1002V |  | 8
 | R9 | Res 0603 | 76.8k | 0603 | Yageo | RC0603FR-0776K8L |  | 1
 | R10 | Res 0603 | 11.5k | 0603 | Yageo | RC0603FR-0711K5L |  | 1
 | R11 | Res 0603 | 24k | 0603 | Panasonic | ERJ-3EKF2402V |  | 1
 | R12, R13, R14 | Res 0603 | 1.5k | 0603 | Yageo | RC0603FR-071K5L |  | 3
 | R15 | Res 0603 | 35.7k | 0603 | Yageo | RC0603FR-0735K7L |  | 1
 | R16, R51, R53 | Res 0603 | 10k | 0603 | Yageo | RC0603FR-0710KL |  | 3
 | R17, R18 | Res 0603 | 4.7k | 0603 | Yageo | RC0603FR-074K7L | DNP | 2
 | R23, R29 | Res 0603 | 84.5 | 0603 | Yageo | RC0603FR-0784R5L |  | 2
 | R24, R30 | Res 0603 | 140 | 0603 | Yageo | RC0603FR-07140RL |  | 2
 | R25, R31 | Res 0603 | 150 | 0603 | Yageo | RC0603FR-07150RL |  | 2
 | R35, R36, R37, R38, R39, R40, R41, R42, R43, R44, R45, R46, R47, R48, R49 | Res 0603 | 4.7k | 0603 | Yageo | RC0603FR-074K7L |  | 15
 | R56, R57, R58 | Res 0603 | 3k | 0603 | Yageo | RC0603FR-073KL |  | 3
 | R59, R60, R68, R69 | Res 0603 | 10k | 0603 | Panasonic | ERJ-3EKF1002V | DNP | 4
 | S1 | Buzzers Transducer, Externally Driven Magnetic 5V 60mA 2.4kHz 88dB @ 5V, 10cm Surface Mount Solder Pads | 88dbA | CT-1205H-SMT-TR | CUI | CT-1205H-SMT-TR |  | 1
 | TP1, TP2, TP3, TP4, TP5, TP6, TP7, TP8, TP9, TP10, TP11, TP12, TP13 | Keystone 5015 SMT Mini Testpoint |  | TP-5015 | Keystone | 5015 |  | 13
 | U1 | STM32F446RE Nucleo MCU Board |  |  | ST | NUCLEO-L452RE | DNP | 1
 | U2 | DC-DC Buck, 60V Input, 3.5A Int Sw, Ultra Low Quiescent Power |  | SOIC8 | Texas Instruments | TPS54360DDAR |  | 1
 | U3, U4, U5 | Pressure Sensor 0.57PSI (3.92kPa) Differential Male - 0.13" (3.3mm) Tube, Dual 1 V ~ 4.9 V 8-BSOP (0.475", 12.06mm Width) Dual Ports, Same Side |  | 8-SOP-MPXV | NXP | MPXV5004DP |  | 3
 | U6 | Watchdog Timer Circuit, 1.6s timeout |  | SOT-23-5 | ST | STWD100NYWY3F |  | 1
 | U8 | Raspberry Pi B+ Footprint direct on PCB |  |  | Raspberry Pi | B+ | DNP | 1
 | U9 | IC I2C SW 4CH W/RESET 20TSSOP |  | 20-TSSOP | Texas Instruments | TCA9544APWR |  | 1
 |  |  |  |  |  |  |  | 200

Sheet: Project Information
Project Full Path | C:\Projects\pcbreathe\RespiraWorks Ventilator.PrjPcb
Project Filename | RespiraWorks Ventilator.PrjPcb
Variant Name | None
Data-Source Filename | RespiraWorks Ventilator.PrjPcb
Data-Source Full Path | C:\Projects\pcbreathe\RespiraWorks Ventilator.PrjPcb
Title | RespiraWorks
Total Quantity | 200
Report Time | 12:33:36 AM
Report Date | 4/25/2020
Report Date & Tine | 4/25/2020 12:33:36 AM
Output Name | Bill of Materials
Output Type | BOM_PartType
Output Generator Name | BOM
Output Generator Description | Bill of Materials

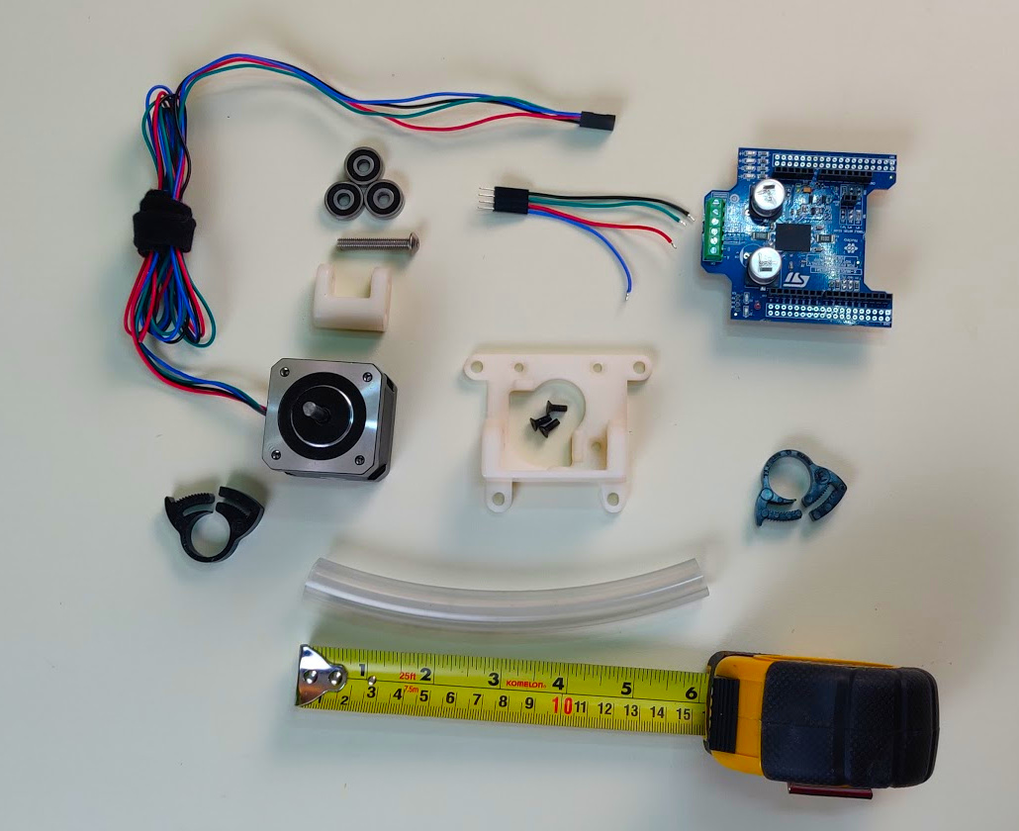
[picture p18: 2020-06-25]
research-development/project-pinch-valve/assets/components.jpg

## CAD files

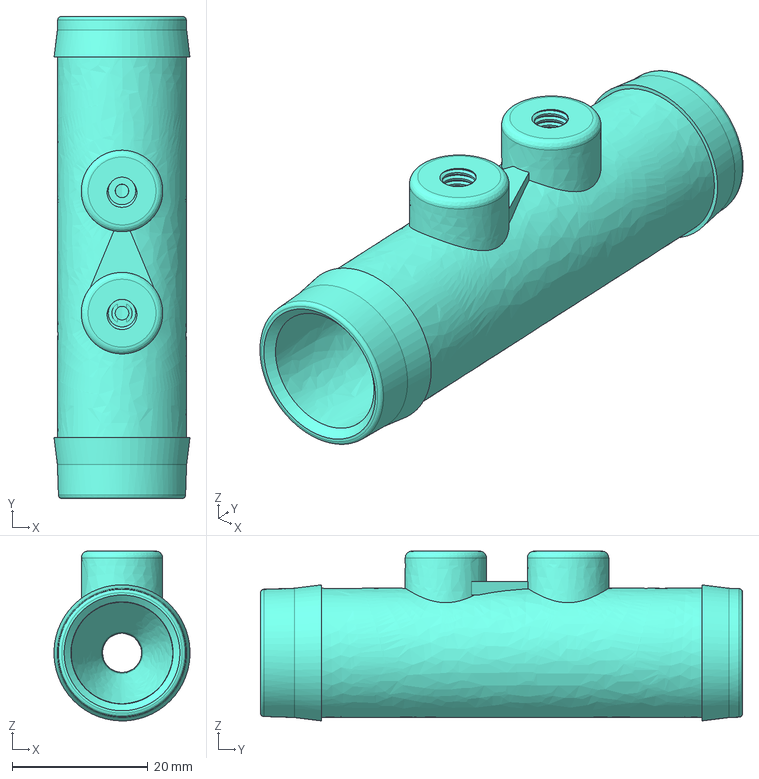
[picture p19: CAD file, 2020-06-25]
research-development/project-venturi/assets/venturi-3-4.iges
20.0 x 71.0 x 25.0 mm

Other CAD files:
manufacturing/alpha-build-instructions/filter-holder/assets/SmallFilterPatientConnector.stl
manufacturing/internals/manifold/oxygen_relief_manifold.stl
manufacturing/internals/pinch_valve/exports/pinch_valve_rotor_011.stl
manufacturing/internals/u_bend_tubing_adapters/u_bend_tubing_adapter_90.stl
manufacturing/internals/venturi/exports/venturi_oxygen_influx.stl
research-development/project-pinch-valve/assets/exhaust-pinch-valve-1.6-base.step
manufacturing/alpha-build-instructions/filter-holder/assets/filter-gasket-jig-inside.stl
manufacturing/internals/pinch_valve/exports/pinch_valve_rotor_008.stl
manufacturing/internals/u_bend_tubing_adapters/u_bend_tubing_adapter_60.stl
research-development/project-pinch-valve/assets/exhaust-pinch-valve-1.6-bearing.step
research-development/project-venturi/assets/venturi-5-8.step
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

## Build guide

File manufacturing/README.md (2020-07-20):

# Ventilator Build

This contains details on the alpha and beta build assemblies, including parts information and assembly instructions.

* [Alpha Build Instructions](alpha-build-instructions)
  * Note: Comprehensive step-by-step assembly instructions [can be found here](assets/covent-june-2020-assembly-instructions.pdf)
* [Beta Build Plan](beta-build-instructions)
* [Production methods for custom components](assets/covent-june-2020-production-methods-for-custom-components.pdf)

# Part Purchasing Guidelines

If you are a member of the RespiraWorks team, please don’t buy anything using personal funds (we need to document everything in specific ways to meet the requirements of our grant funding).

Before purchasing any parts, **ask** team members (the [#dev-hardware](https://respiraworks.slack.com/archives/C012UTERXD5) RespiraWorks Slack channel is a good place to start) if they have any spare parts floating around. There are a lot of extras, so you may be able to get your hands on parts without ordering anything.

If you do need to purchase parts, follow the process below. Note: This process is subject to change as we work out any issues. Message Curtis Kline with any questions.

1. If you need to buy something, put the details into a post in [#purchasing-sourcing](https://respiraworks.slack.com/archives/C011FD2TEQM) (RespiraWorks Slack channel) and tag the [@purchasing group](https://respiraworks.slack.com/admin/user_groups).
2. One of the Purchasing team members will source the items and confirm with you before placing the order (unless it’s obvious).
3. Everything will be purchased using a RespiraWorks credit card whenever possible.
4. The Purchasing team member will reply to your message in [#purchasing-sourcing](https://respiraworks.slack.com/archives/C011FD2TEQM) with tracking info when available.
5. in the rare case that you do buy something urgent with your own payment methods, submit your receipts to #accounting-reimburse.

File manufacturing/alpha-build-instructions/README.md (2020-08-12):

# Alpha Prototype

-------------

**DISCLAIMER: These are live documents.
There are duplicate and alternative items for undecided aspects of the physical design.
RespiraWorks may, or may not compensate you for any of these parts.
If you decide to buy them, do so at your own risk.**

[**Brain build**](pizza-brain) constitutes just the computing components.

[**Pizza build**](pizza-build.md) is an upgrade that includes sensors, drivers and pneumatics.
Lives on your table and is customizable, like a pizza. Here are the various components:

* [Mandatory blower assembly](pizza-blower)
* [Mandatory basic test lung](pizza-test-lung)
* [Mandatory flow sensors](../../research-development/project-venturi)
* [Optional: binary solenoid assembly](pizza-binary-solenoid)
* [Optional: proportional pinch valve assembly](../../research-development/project-pinch-valve)
* [Optional: reduced compliance test lung](pizza-compliance-test-lung)
* [Optional: air filter assembly](filter-holder)

[Enclosed alpha assembly instructions](alpha-assembly-instructions.md)

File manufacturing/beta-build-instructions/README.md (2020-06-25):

# Beta Build Plan

This page contains a running list of notes and planned updates that will be organized and added to as we get further into beta design and build.

## Venturi Updates

We're planning to use 3/4"ID tubing throughout. The venturi will most likely be redesigned to have barbs that fit 3/4" ID tubing directly.

## Nucleo Module Updates

We're planning to move the STM32 onto the PCB, so there won't be a need to buy nucleo module.

## STM32 Updates

We're planning to add some kind of Flash memory to support non-volatile storage of configuration parameters. Part selection is still TBD; we'll either be moving to dual flash bank STM32 or add an i2c EEPROM (already planned for PCB Rev A).

## Stepper Drivers Updates

We're planning to move the steppers driver onto the PCB. Because of this, there will be no need to buy stepper drivers.

## RTC Battery

We're planning to add an RTC battery, which will allow controller to keep track of time while off - Pizza build no change, this feature not available for now

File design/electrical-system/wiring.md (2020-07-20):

# Wiring

**DISCLAIMER: These are live documents.
There are duplicate and alternative items for undecided aspects of the physical design.
RespiraWorks may or may not compensate you for any of these parts if you choose to buy them. Please connect with Edwin or Ethan first.
If you decide to buy them, do so at your own risk... oh, and thank you ;).**

**TODO:** explain purpose and contents

## Parts List (BOM)

**Note: If you are a member of the RespiraWorks team, review [part purchasing guidelines](../../manufacturing/README.md) BEFORE purchasing any parts.**

### Purchasing Source Abbreviations

* **Z** = Amazon
* **K** = Digikey

### Parts

| RefDes | Quantity | Manufacturer  | Part #              | Price($)     | Sources         | Notes |
| ------ |---------:| ------------- | ------------------- | ------------:|-----------------| ----- |
| 1      |       12 | JST           | SXH-001T-P0.6       |         0.10 | [K][1digi]      | XH crimps, for sensor & actuator connections |
| 2      |        - | JST           | XHP-2               |         0.10 | [K][2digi]      | XH 2-pin housings, for solenoid |
| 3      |        - | JST           | XHP-3               |         0.10 | [K][3digi]      | XH 3-pin housings, for heater |
| 4      |        - | JST           | XHP-5               |         0.12 | [K][4digi]      | XH 5-pin housings, for sensors |
| 5      |        2 | JST           | XHP-6               |         0.12 | [K][5digi]      | XH 6-pin housings, for blower control |
| alt1   |        - | WGCD          | 4330589508          |         8.99 | [Z][alt1amzn]   | XH connector kit for 2/3/4/5 pins, alternative for 1+2+3+4 above |
| alt2   |        - | CQRobot       | CQRJST254-BGB       |         9.99 | [Z][alt2amzn]   | XH connector kit for 6/7/8 pins, alternative for 1+5 above |
| 6      |        6 | JST           | SVH-21T-P1.1        |         0.11 | [K][6digi]      | VH crimps, for power connectors |
| 7      |        2 | TE            | 1-1123722-2         |         0.18 | [K][7digi]      | VH housing 2 pin, for blower power |
| 8      |        1 | JST           | VHR-3N              |         0.14 | [K][8digi]      | VH housing 3 pin, for main power |
| 9      |        1 | AIMHD         | AHD-DC20-F-PT       |    9.99 / 20 | [Z][9amzn]      | Female Power Pigtail DC 5.5mm x 2.1mm Connectors, for main power |
| 10     |        - | Remington     | 16UL1007STRKIT      |        29.70 | [Z][10amzn]     | 16 AWG wire, for blower power cable |
| 11     |        - | Remington     | 26UL1007STRKIT10COLOR |      31.60 | [Z][11amzn]     | 26 AWG wire, for signal/control cables |
| 12     |        - | Remington     | 22UL1015STRKIT10COLOR |      37.75 | [Z][12amzn]     | 22 AWG wire, for signal/control cables |

[1digi]:    https://www.digikey.com/short/z44f8d
[2digi]:    https://www.digikey.com/short/z44f8f
[3digi]:    https://www.digikey.com/short/z44fb9
[4digi]:    https://www.digikey.com/short/z44r0b
[5digi]:    https://www.digikey.com/short/z44ff8
[alt1amzn]: https://www.amazon.com/gp/product/B06ZZ45G7G
[alt2amzn]: https://www.amazon.com/gp/product/B079MJ1RYN
[6digi]:    https://www.digikey.com/short/z44fjr
[7digi]:    https://www.digikey.com/short/z44fwj
[8digi]:    https://www.digikey.com/short/z44fwp
[9amzn]:    https://www.amazon.com/Connectors-Upgraded-Surveillance-Transformer-Connection/dp/B0768V9V5Q
[10amzn]: https://www.amazon.com/gp/product/B00N51OJJ4
[11amzn]: https://www.amazon.com/gp/product/B011JC76OA
[12amzn]: https://www.amazon.com/gp/product/B073SDGNKW

### Tools

We try to make few assumptions about what tools you have. Here are recommended tools you might need.

| Item | Quantity | Manufacturer  | Part number         | Price($) | Sources         | Notes |
| ---- |---------:| ------------- | ------------------- | --------:|-----------------| ----- |
| T1   |        1 | Preciva         | PR-3254 (PR102001)             |    39.99 | [Z][t1amzn]     | Crimping tool for HX and HV connectors |

[t1amzn]:https://www.amazon.com/gp/product/B07R1H3Z8X

**Crimper Tips:**

* Position 1 on the crimper will crimp XH contacts
* Position 2 on the crimper will crimp VH contacts.  However, with certain gauges of wire, this crimper may bend the contact into a shrimp-like shape.  If this happens, bend the contact back straight (it should be pretty obvious as it blocks insertion)
* It comes with a lot of XH contacts, but not any VH contacts.

## Assembly

As much as possible we should try to keep the cables one-to-one
(for example the wiring of the PCB to blower driver cables are all pin 1 to pin 1,
pin 2 to pin 2, etc. with the same connector style on both ends.

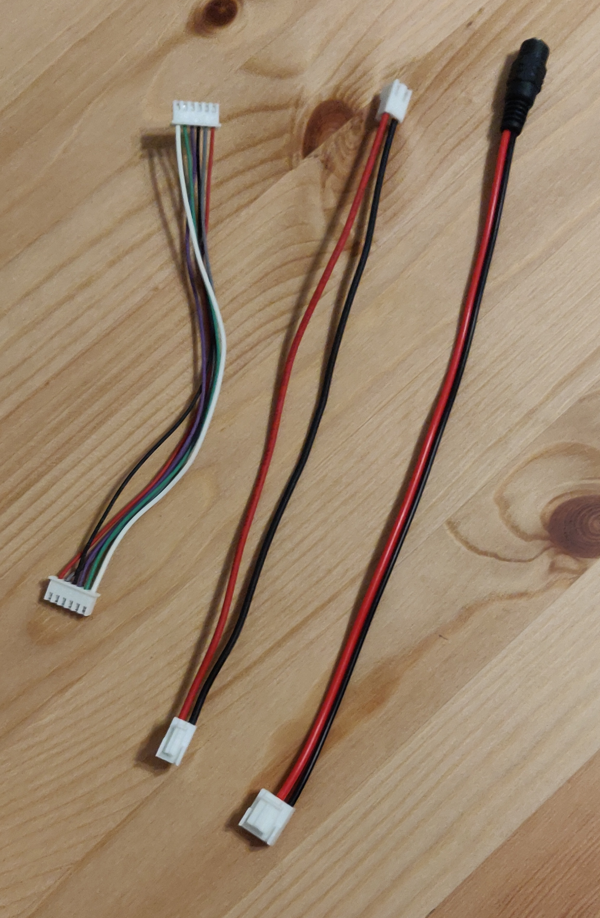
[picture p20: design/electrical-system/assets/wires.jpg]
Pizza pneumatics


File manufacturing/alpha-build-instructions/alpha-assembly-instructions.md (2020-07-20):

# Alpha Assembly Instructions

Ventilator under construction

1. Mount the rPi to the back of the rPi display. Connect display cables.
2. Identify [Front Panel - Inner] and determine the inside and outside of the panel. Mount the following components to the panel:
    1. Outer side: rPi display + rPi, inhale and exhale ports, filter housing, O2 barb
    2. Inner side: Blower, Arduino, Pressure sensor board, blower driver
3. Complete wiring connections between pressure sensor board, arduino, rPi, and blower driver
4. Bolt the power port to [Front Panel - Outer], with the jack facing out and set aside.
5. Slot [Gusset] into [Front Panel - Inner] - hold it in final position indicated in CAD model
6. Slot [Shelf Panel] into place, by doing the following:
    1. slot [Shelf Panel] over the bottom tabs of [Gusset] until tabs have fully passed through
    2. shift [Shelf Panel] forward towards [Front Panel - Inner] until the tabs on [Shelf Panel] have fully slotted through the slots on [Front Panel - Inner]
    3. shift [Shelf Panel] left - relative to [Front Panel - Inner] and [Gusset] - to lock tabs into place in both [Gusset] and [Front Panel - Inner]
7. Slot [Front Panel - Outer] onto the front of [Front Panel - Inner], locking the position of all tabs.
8. Add bolts, washers, and lock nuts through 4x 1/4-20 mounting holes in the front of [Front Panel - Outer] - _note: for final assembly, this bolt stack should include the enclosure lid. For prototyping, the lid may be omitted, however, adding the 1/4-20 bolts is important for the purpose of keeping all tabbed connections tight._
9. Create a subassembly of the following parts, including short hose sections and hose clamps where needed (see model):
    1. brass elbow
    2. inhale venturi
    3. brass hose barb
    4. plastic tee
    5. overpressure relief valve (or NPT plug, if valve has not arrived)
    6. brass hose barb
10. Make a tubing connection between the previous assembly and the back side of inhale port. Secure subassembly to plastic structure using zip-tie loops through provided slots.
11. Make a tubing connection between the exhale venturi and the back side of the exhale port. Secure venturi to plastic structure using zip-ties.
12. Create a subassembly of the following parts, including short hose sections and hose clamps where needed (see model):
    1. brass elbow
    2. check valve
    3. plastic nipple
    4. plastic tee
    5. small brass hose barb
    6. brass elbow
13. Make a tubing connection between the previous assembly and the blower outlet. Secure subassembly to plastic structure using zip-ties.
14. Make a tubing connection between the oxygen inlet port and the mixing tee.
15. Create a subassembly of the following parts (see model):
    1. brass elbow
    2. solenoid
    3. brass elbow
16. Secure previous subassembly to plastic structure using zip-ties. Solenoid flow direction goes towards [Gusset].
17. Complete wiring connection between power inlet port and boards, and solenoid if needed.
18. Create tubing connections between venturi pressure ports and differential pressure sensors. Include a Y tubing splitter on the outlet of the inhale venturi to read patient pressure.
19. Make the following tubing connections to complete the flow circuit:
    1. outlet of oxygen mixing tee to inlet of inhale venturi
    2. exhale venturi to inlet of solenoid
    3. outlet of solenoid to exhaust filter port
    4. blower inlet to inlet filter port
20. If enclosure lid was included in assembly, snap lid onto enclosure to complete the ventilator assembly. Add external viral filtration, humidifier chamber, and breathing circuit.

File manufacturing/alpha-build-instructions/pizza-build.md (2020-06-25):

# Pizza Build

**WARNING: This is not intended to be used on patients and lacks a number of safety features.**

This is a ventilator prototype for testing and development.
The build consists of a functional ventilator pneumatic assembly with controller and user interface. This build is adequate for integration and systems testing.

It lacks heating, humidification, battery backup and air filtering.

It is also not enclosed like the final product and is meant to be operated in an open layout on your table, like a pizza.

It can also come in various configurations, depending on your testing needs:

| Solenoid valve setup  |  Pinch valve setup   | Blower bypass setup     |
|:---------------------:|:--------------------:|:-----------------------:|
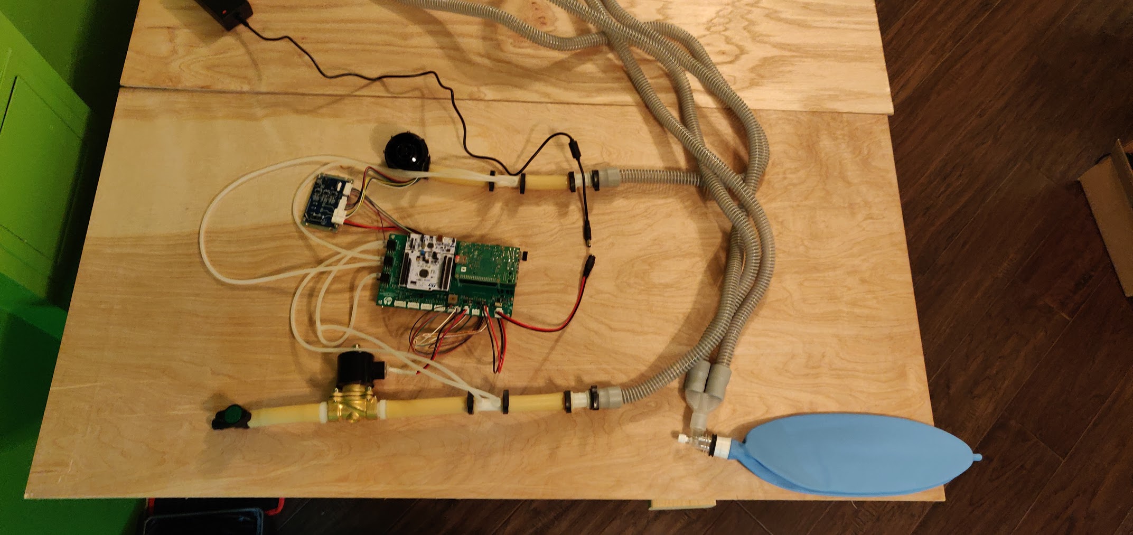
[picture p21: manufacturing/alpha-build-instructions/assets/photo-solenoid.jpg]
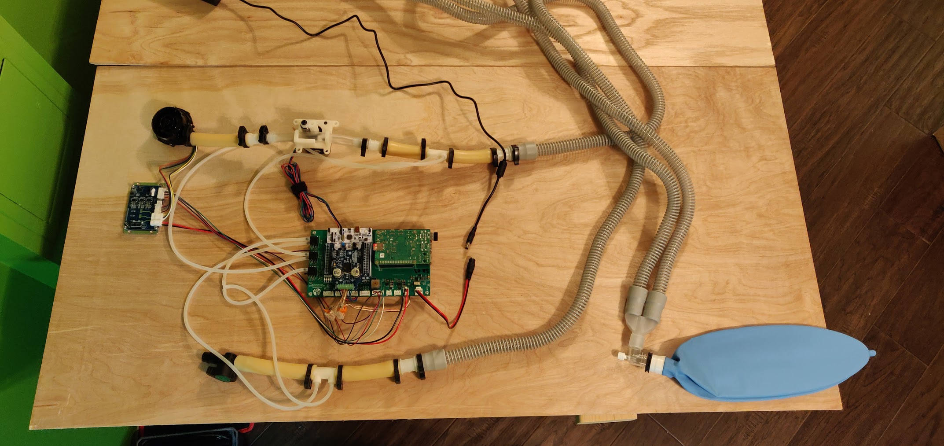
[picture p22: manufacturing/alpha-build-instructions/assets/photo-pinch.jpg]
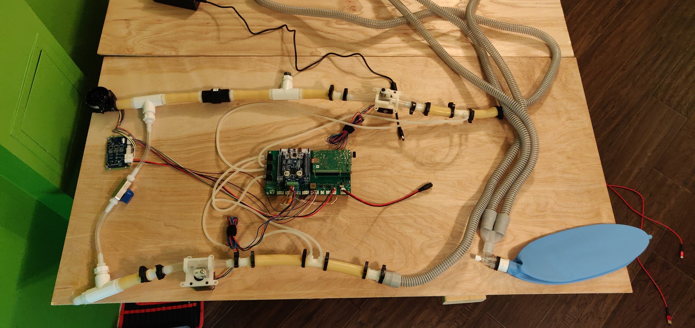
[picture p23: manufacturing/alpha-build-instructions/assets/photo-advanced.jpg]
 |  |  |

**DISCLAIMER:** These are live documents.
There are duplicate and alternative items for undecided aspects of the physical design.

RespiraWorks may or may not compensate you for any of these parts if you choose to buy them. Please connect with Edwin, Martin or Ethan first.
If you decide to buy them, do so at your own risk... oh, and thank you ;).**

## Planning

Before you start, it would be wise to plan the configuration you will build and order adequate amounts of components.
Try to plan for what you'll need in a few weeks rather than what you need now.
Supply chains are quirky and shipping times can be long, so your surprise at having missed something will soon turn to frustration.
The goal of this documentation has been precisely to help you avoid unproductive waiting. **PLAN NOW!**

Read over as much of the following documentation as you can and then come back to this point.

Now, contact the team to see if we have components in stock that we can send you.
Once you know what you are getting from "headquarters", only then should you start filling up your baskets.
Also ask the team if anything should be ordered on the company account.

## Essentials

The first thing you will need is a [Brain build](pizza-brain), which contains the computing components.

We are using 3/4" ID tube as the default standard (and adapters where needed, like to the blower and the pinch valves).
This easily can have 19mm ID tubing substituted in metric manufacturing settings (3/4" = 19.05mm).
All rigid plumbing fittings should be NPT/imperial standard (3/4 NPS preferable, to keep ID consistent throughout the flowpath).

## Parts List (BOM)

**Note: If you are a member of the RespiraWorks team, review [part purchasing guidelines](../README.md) BEFORE purchasing any parts.**

### Purchasing Source Key

* **Z** = Amazon
* **C** = McMaster-Carr

### 3/4" ID Tubing Components

| Item | Quantity | Manufacturer  | Part #              | Price (USD)     |  Sources       | Notes |
| ---- |---------:| ------------- | ------------------- | ------------:|----------------| ----- |
| a1   |      5ft |      OCSParts |            117062-5 | 22.99 / 5ft  | [Z][a1amzn]    | soft 3/4"ID 1"OD tubing |
| a2   |      5ft | McMaster-Carr | 5233K71             | 14.20 / 10ft | [C][a2mcmc]    | hard 3/4"ID 1"OD tubing, **alternative to a1**, not as fun to work with, not for medical use |
| a3   |        6 | McMaster-Carr | 9579K73             | 12.24 / 20   | [C][a3mcmc]    | Herbie clip K (22.2-24.9mm) for clamping 1"OD tubing, works better for soft tubing |
| a4   |        6 | McMaster-Carr | 9579K74             | 12.33 / 20   | [C][a4mcmc]    | Herbie clip L (24.5-27.6mm) for clamping 1"OD tubing, **alternate to a3** maybe works better for hard tubing? |
| a5   |        1 | McMaster-Carr | 5463K648            | 10.20 / 10   | [C][a5mcmc]    | 3/4"ID <-> 3/8"ID adapter, to interface with pinch valve tubing |

[a1amzn]: https://www.amazon.com/gp/product/B01LZ5ZK53
[a2mcmc]: https://www.mcmaster.com/5233K71
[a3mcmc]: https://www.mcmaster.com/9579K73
[a4mcmc]: https://www.mcmaster.com/9579K74
[a5mcmc]: https://www.mcmaster.com/5463K648

### Metric Version

**#TODO: document how to build with metric components**

### Tools

Assembling the pneumatic system will likely need the following tools.
T1 might be enough and T4 might be unnecessary.
Also, scissors or a sharp knife might be ok instead of T3.

| Item | Manufacturer  | Part number        | Price (USD) | Sources         | Notes |
| ---- |--------------:| ------------------ | -------- | ---------------:|------ |
| c1   |        TEKTON |              37122 |    13.00 | [Z][c1amzn]     | 8 inch slip-joint pliers, for clamping tubes onto fittings |
| c2   |   Duda Energy |     LPpvc075-005ft |    19.99 | [Z][c2amzn]     | Adjustable wrench, at least 1" wide opening, for screwing in NTP fittings |
| c3   |        DEWILL |          (unknown) |    15.88 | [Z][c3amzn]     | Pipe and PVC cutter, for cutting tubing |
| c4   |         IRWIN |            2078216 |     8.90 | [Z][c4amzn]     | Long nose pliers, for removing herbie clips |
| c5   |          PTFE | vanguardSealantsPTFE-01 |     6.49 | [Z][c5amzn]     | It's advisable to teflon tape all NTP threaded components. Not only will they be more airtight, but also they will be easier to tighten and release. |

[c1amzn]: https://www.amazon.com/TEKTON-2-Inch-Joint-Pliers-37122/dp/B00KLY1FAY
[c2amzn]: https://www.amazon.com/GETUPOWER-10-Inch-Adjustable-Opening-Vanadium/dp/B07RGV2VK1
[c3amzn]: https://www.amazon.com/gp/product/B07Y997XKC
[c4amzn]: https://www.amazon.com/Tools-VISE-GRIP-Pliers-6-Inch-2078216/dp/B000A0OW2M
[c5amzn]: https://www.amazon.com/gp/product/B01L2F428C

## Sub-assemblies

The following are essential sub-assemblies that you'll need no matter what additional/optional "toppings" you chose to have.

* [Blower assembly](pizza-blower) - the main driver of pressure in the pneumatic circuit
* [Basic test lung](pizza-test-lung) - something to simulate a lung
* 2x [Venturi flow sensors](../../research-development/project-venturi) and corresponding tubing, to provide the controller feedback
* Some sort of valve or valves, which leads us to...

## Optional Components

**Optional additions (toppings) for your pizza build:**
These can be added or customized based on what functions you will be developing or testing.

* **Binary solenoid:** One option for inhale or exhale valve is a binary solenoid, which either opens or closes.
The sub-assembly for this component is documented [here](pizza-binary-solenoid). The PCB can only power/control one such
solenoid, so for more advanced designs you will want to (also) start using other valves.
* **Proportional pinch valve:** A proportional pinch valve can control the airflow constriction with much better precision.
Multiple such pinch valves can be used in our prototype, the part is buildable from 3d-printed plastic components and
easily obtainable generic parts. Instructions are [here](../../research-development/project-pinch-valve).
You may need anywhere between 1 and 3 such pinch valves, depending on the complexity of your system.
* **Reduced compliance test lung:** To test basic function a ventilator check lung or a breathing bag is sufficient,
but can really only work up to 10cmH2O. To be able to test higher PIP values, you need to reduce the compliance of the
lung so you don’t just inflate it like a balloon (or pop it). View more details on reduced compliance test lung [here](pizza-compliance-test-lung).
* **#TODO: check valve**
* **#TODO: oxygen supply limb**

## Assembly Instructions

Use the following diagrams as well as the pictures of the most recent builds at the top of the page to help you assemble this lego set.

Pizza pneumatics
[Pneumatics diagram source](assets/pizza-pneumatics.eps)

Note: mind which tubes go into the bottom and top ports of the sensors on the PCB.

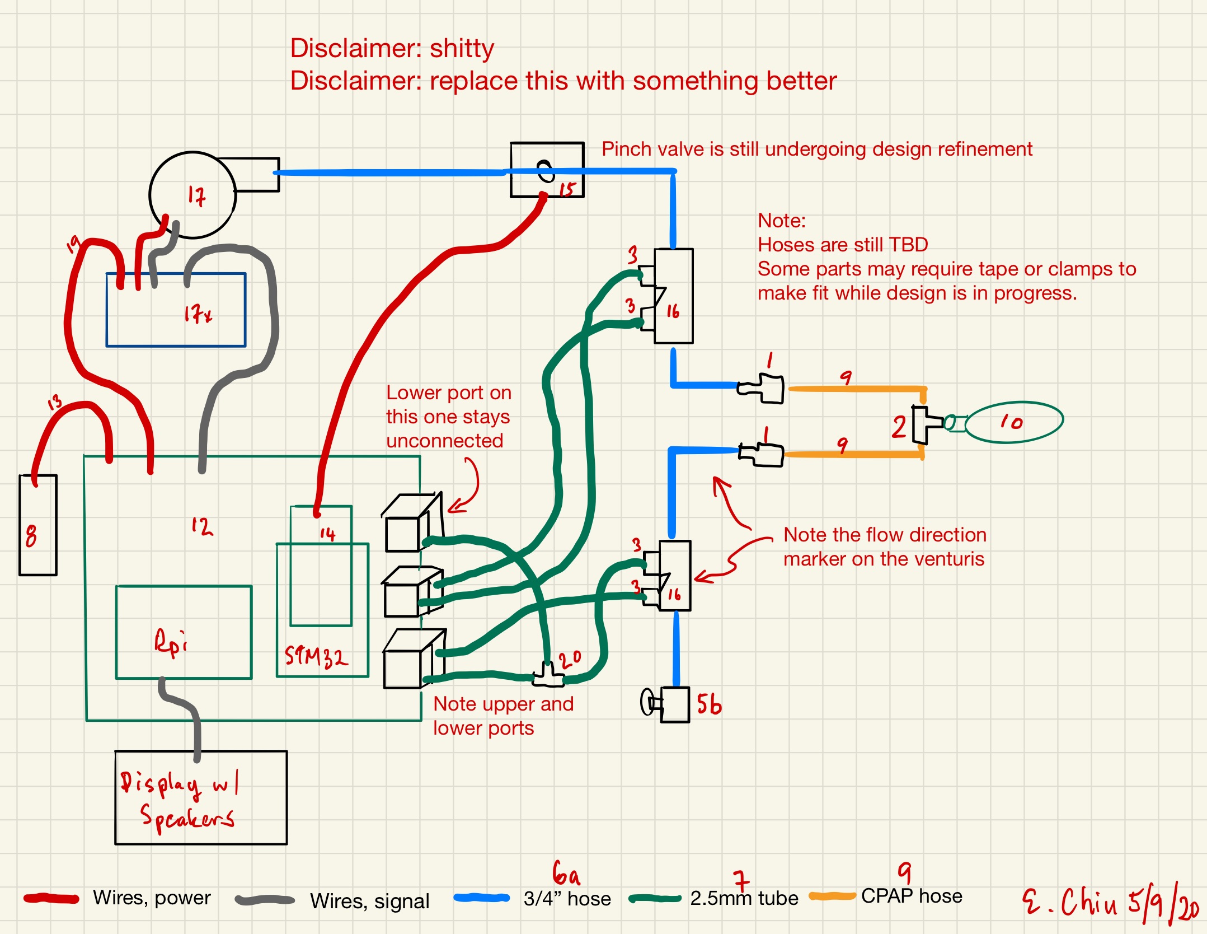
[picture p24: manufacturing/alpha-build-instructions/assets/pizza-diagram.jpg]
Pizza drawing


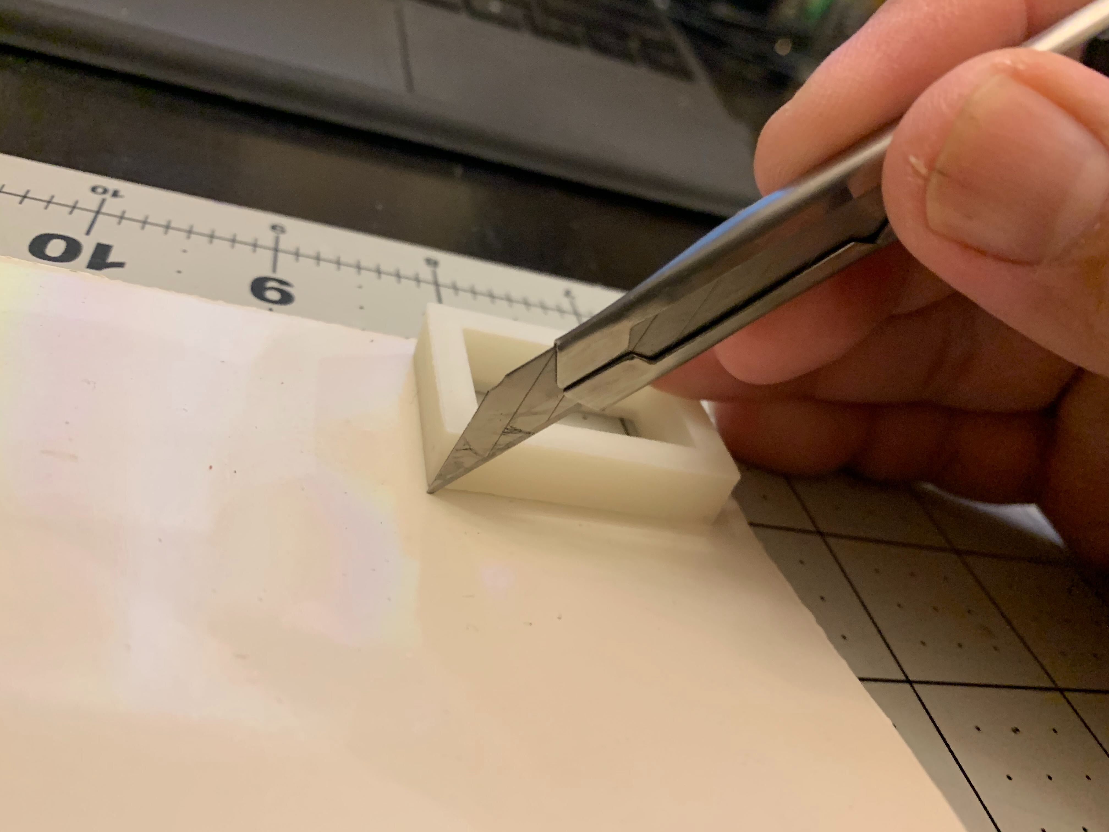
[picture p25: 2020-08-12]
manufacturing/alpha-build-instructions/filter-holder/assets/MakeGasket5.jpg

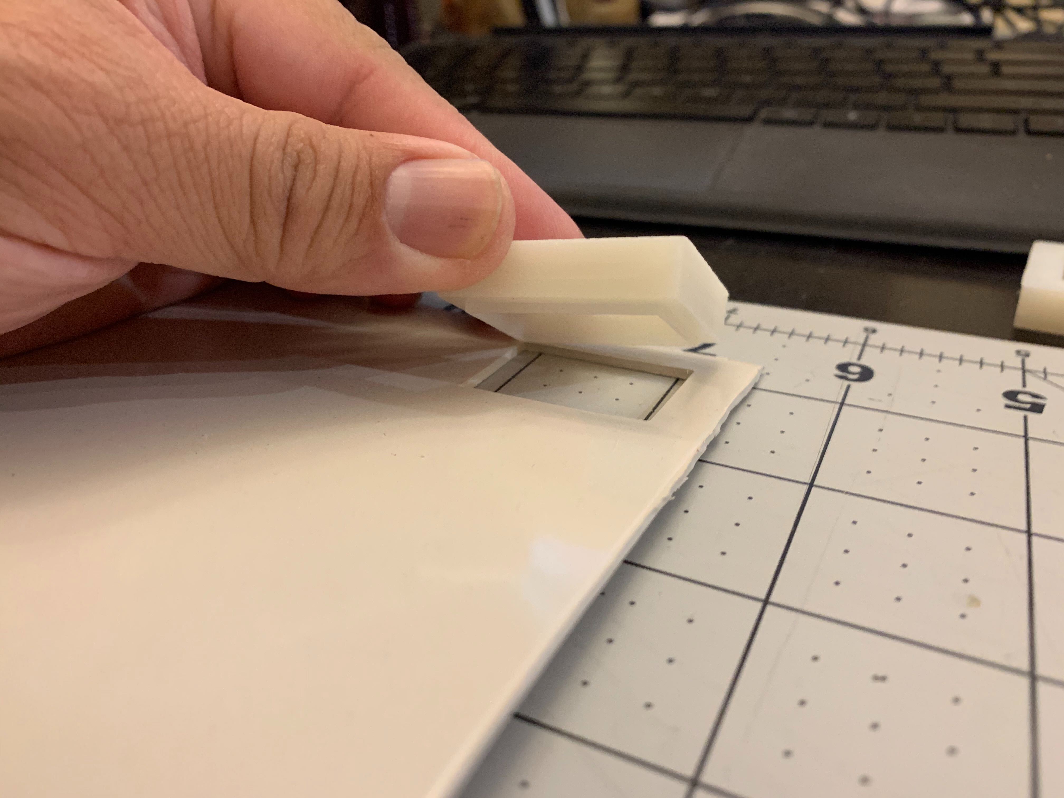
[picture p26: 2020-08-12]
manufacturing/alpha-build-instructions/filter-holder/assets/MakeGasket4.jpg

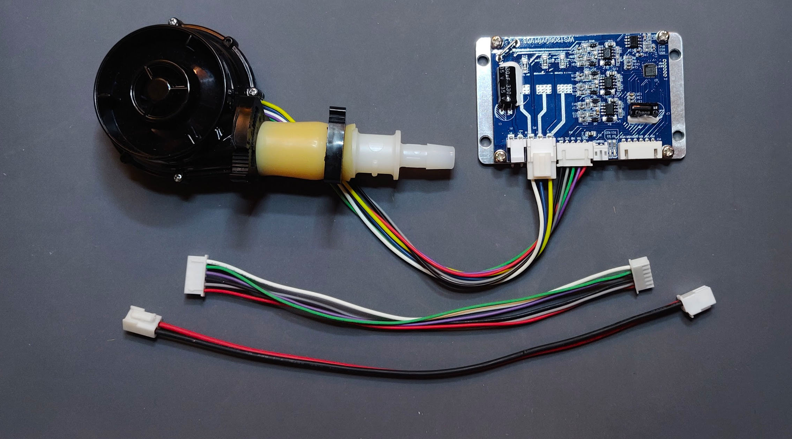
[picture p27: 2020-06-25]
manufacturing/alpha-build-instructions/pizza-blower/assets/subassembly.jpg

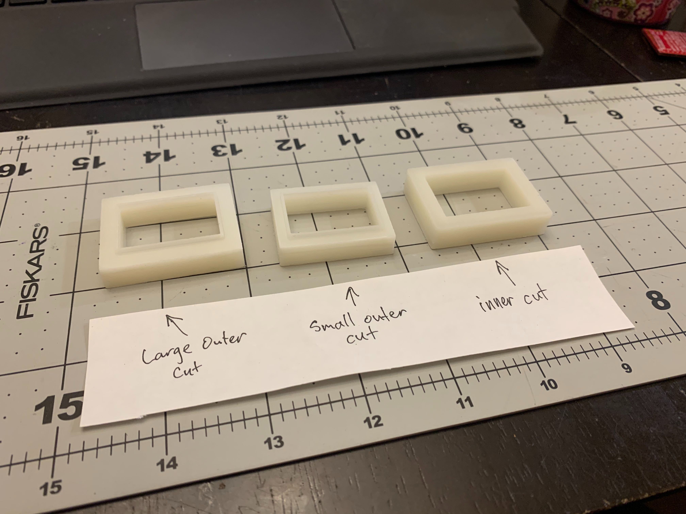
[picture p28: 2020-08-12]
manufacturing/alpha-build-instructions/filter-holder/assets/MakeGasket1.jpg

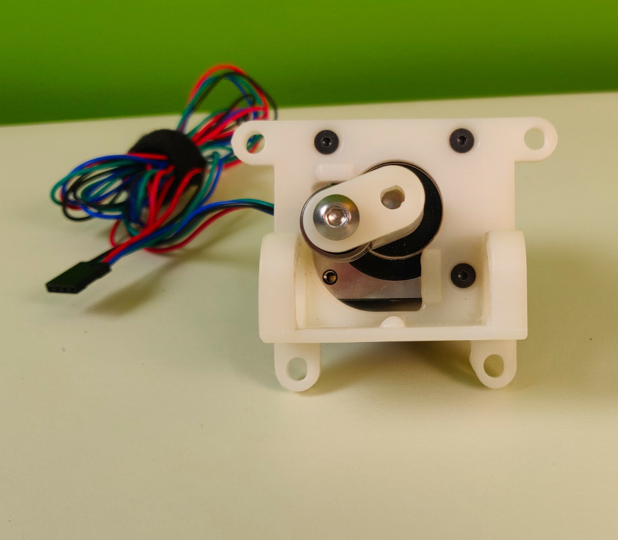
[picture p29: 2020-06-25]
research-development/project-pinch-valve/assets/assembled_smaller.jpg

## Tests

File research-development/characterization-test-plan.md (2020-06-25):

# Characterization Test Plan

This document will track desired characterization tests and link to the corresponding data when the test is performed. Eventually the info from this document will likely be formalized into a record of tests that have been performed as part of the development and validation of the ventilator - integration tests with the real software are expected to be defined elsewhere, though they could be folded into this.

**Caution:** this document has not been formally reviewed and is a work in progress. Be responsible to understand the provenance of documentation.

**NOTE:** these tests are supposed to be iteratively developed. As we progress, the tests will become more granular.

## System Characterization

* **Fan Tests**

**#TODO** Add content

[View fan tests](project-fan/characterization-tests)

* **PIP/PEEP/Timing Tests**

    1. What is the maximum pressure that can be achieved with the current blower with a representative amount of tubing, a fully open air inhale valve, and a fully closed exhale valve?

    2. From PEEPs of 0 to 20 cm H20 (in reasonable increments), how quickly can the current design achieve PIPs from 10 cm H20 up to 60 cm H20 (or the max value, testing reasonable increments)?

    3. From PIPs from 20 cm H20 up to 60 cm H20 (or however high can be achieved, in reasonable increments), how quickly can the system vent down to PEEPs of 0 to 20 cm H20 (testing reasonable increments)?

    4. For PIPs from 20 cm H20 up to 60 cm H20 (in reasonable increments), what is the maximum flow rate into the patient that can be achieved? How does this change as a function of how much the exhaust valve is open?

    5. For 1-4 with a flow source that is better than the blower, what can be achieved (what becomes the next lim fac)?

* **System Sensitivity Tests**

    1. What is the difference in pressure right after the inhale venturi (before the humidifier) and at the patient pressure sensor before the exhale venturi?

## Valve Tests

* **Pinch Valve Characterization**

    1. How quickly can the pinch valve be fully opened? How does this change as a function of pressure (up to at least 60 cm H20)?

    2. How quickly can the pinch valve be fully closed? How does this change as a function of pressure (up to at least 60 cm H20)

    3. What is the leak rate past a fully closed pinch valve as a functin of pressure (up to at least 60 cm H20)?

* **Proportional Solenoid Characterization**

    1. How quickly can the solenoid be fully opened? How does this change as a function of pressure (up to at least 60 cm H20)?

    2. How quickly can the solenoid be fully closed? How does this change as a function of pressure (up to at least 60 cm H20)

    3. What is the leak rate past a fully closed soleonid valve as a function of pressure (up to at least 60 cm H20)?

## Sensor Tests

* **DP sensor/Venturi characterization**

    1. For flow rates from 1 to 80 lpm, how accurate is the flow measurement and how does this accuracy change over time (if sitting at a specific FiO2)?

    2. How do the measurements for letter i above change as a function of temperature and humidity?

    3. How do the measurements for letter i above change as a function of the flow rate that is being started at (e.g. if you go from 1->80 or 40->80 does the accuracy change? What about 80->1 and 80->40)?

    4. When there is a change in flow rate, how long does it take for the sensor to settle?

    [View Venturi tests](project-venturi/characterization-tests/06072020/README.md)

* **Pressure sensor characterization**

    1. For pressures from 1 to 60 cm H20, how accurate is the pressure reading and how does this accuracy change over time (if sitting at a specific FiO2)?

    2. How do the measurements for letter i above change as a function of temperature and humidity?

    3. How do the measurements for letter i above change as a function of flow rate past the sensor?

    4. How do the measurements for letter i above change as a function of the pressure that is being started at (e.g. if you go from 5->60 or 30->60 does the accuracy change? What about 60->5 and 60->30)?

    5. When there is a change in pressure, how long does it take for the sensor to settle?

* **O2 sensor characterization**

    1. For FiO2s from 21% to 100%, how accurate is the o2 sensor reading and how does this accuracy change over time (if sitting at a specific FiO2)?

    2. How do the measurements for #1 change as a function of temperature and humdity?

    3. How do the measurements from #1 change as a function of flow rate?

    4. When there is a change in FiO2, how long does it take for the sensor to settle?

## Things that need to be added

* #todo Add electronics/Software/Controller tests?

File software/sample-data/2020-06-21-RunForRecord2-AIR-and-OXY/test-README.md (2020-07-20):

# 2020-06-21 CoVent Run for Record (AIR and OXY)

* **Date of test:** 2020-06-21

* **Tester:** Edwin Chiu edwin@respira.works

* **Software version**: [b514f94](https://github.com/RespiraWorks/Ventilator/commit/b514f94b0de66710a43f8e3bb138cbb976c54fca)

* **Test data:** [Link to file](https://github.com/RespiraWorks/Ventilator/tree/master/software/sample-data/2020-06-21-RunForRecord2-AIR-and-OXY)

* **Summarize test setup's main components:**
  * Pizzabuild SN01 (Edwin) Inhale and Exhale pinch valves, oxygen PSOL

* **User settings (specify here or in test file):**
    * **PIP (cmH20):** CoVent tests 1-8 as defined in 80601 Table 201.105
    * **PEEP (cmH20):** CoVent tests 1-8 as defined in 80601 Table 201.105
    * **RR (bpm):** CoVent tests 1-8 as defined in 80601 Table 201.105
    * **IE Ratio:** CoVent tests 1-8 as defined in 80601 Table 201.105
    * **FiO2 (%):** Tests 1-8 run with 21% FiO2 (pure air) and 100% FiO2 (pure oxygen)
    * **Ventilator Mode**: Pressure Assist
    * Alarm settings if relevant: N/A

* **Lung values:**
    * **Type of test lung used:** IngMar QuickLung
    * **Compliance (ml/cmH20):** CoVent tests 1-8 as defined in 80601 Table 201.105
    * **Resistance (cmH20/L/s):** CoVent tests 1-8 as defined in 80601 Table 201.105
* **Are sensor readings included in the file?**: Patient pressure and net flow are included

* **Are controller commands to each of the actuators included in the file?**: No

* **Open loop state actuators - provide info here or specify that they are contained in the file:**
    * **Blower speed on inhale:** 100%
    * **Blower speed on exhale:** 100%
    * **Exhale Valve state on inhale (AIR):** Closed loop 1.0f - 0.55f * blower_valve - 0.4f
    * **Exhale Valve state on exhale (AIR):** Closed loop 1.0f - 0.55f * blower_valve - 0.4f
	* **Exhale Valve state on inhale (OXY):** Closed loop 1.0f - 0.6f * psol_valve - 0.4f
    * **Exhale Valve state on exhale (OXY):** Closed loop 1.0f - 0.6f * psol_valve - 0.4f

* **Controller gains used (or other relevant controller information)**
    * **Kp:** 0.04
    * **Ki (AIR):** std::clamp(1.0f * (desired_state.pip - desired_state.peep).cmH2O() - 5.0f, 10.0f, 20.0f)
	* **Ki (OXY):** 20.0
    * **Kd:** 0.0

* **Information about mappings to/from controller (either provide mapping or pont to where in the code this is done):**
    * **Pressure sensor voltage to controller value mapping:** /controller/lib/core/sensors.cpp
    * **Air pinch valve command to voltage mapping:** /controller/lib/core/pinch_valve.cpp
    * **Ox PSOL valve command to voltage mapping:** /controller/lib/hal/psol.cpp

* **Any other hardware settings that have been variable or might change** *(e.g. the bit resolution for the raw sensor valves):*
  * [Details here]

* **Images**

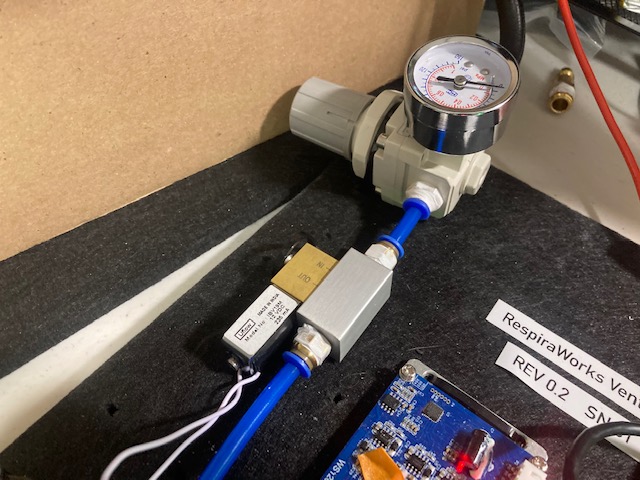
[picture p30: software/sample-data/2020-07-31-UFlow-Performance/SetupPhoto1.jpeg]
Setup Photo 1


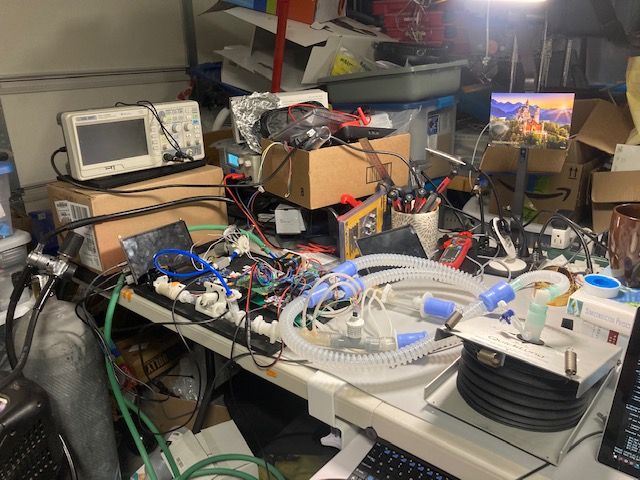
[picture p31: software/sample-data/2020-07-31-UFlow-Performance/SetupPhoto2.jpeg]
Setup Photo 2


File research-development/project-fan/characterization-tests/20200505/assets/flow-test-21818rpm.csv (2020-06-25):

t | p1_adc | patient | p2_adc | p2 | p3_adc | p3 | Q1
0.05 | 457.0 | 1.186104218362283 | 580.0 | 1.7855361596009975 | 629.0 | 2.0150753768844223 | 66.27393128634002
0.1 | 448.0 | 1.1414392059553349 | 632.0 | 2.0448877805486285 | 663.0 | 2.185929648241206 | 70.92398808883199
0.15 | 480.0 | 1.3002481389578164 | 557.0 | 1.6708229426433916 | 641.0 | 2.0753768844221105 | 64.109682099571
0.2 | 461.0 | 1.205955334987593 | 638.0 | 2.0748129675810474 | 600.0 | 1.8693467336683418 | 71.44105924624942
0.25 | 482.0 | 1.3101736972704714 | 629.0 | 2.029925187032419 | 616.0 | 1.949748743718593 | 70.6640336842167
0.3 | 440.0 | 1.1017369727047146 | 601.0 | 1.8902743142144638 | 627.0 | 2.0050251256281406 | 68.1900210987737
0.35 | 435.0 | 1.0769230769230769 | 593.0 | 1.8503740648379052 | 620.0 | 1.9698492462311559 | 67.46649907706849
0.4 | 468.0 | 1.2406947890818858 | 625.0 | 2.0099750623441395 | 632.0 | 2.030150753768844 | 70.31593287908903
0.45 | 451.0 | 1.1563275434243176 | 622.0 | 1.9950124688279303 | 640.0 | 2.07035175879397 | 70.05372214776233
0.5 | 461.0 | 1.205955334987593 | 617.0 | 1.9700748129675811 | 633.0 | 2.0351758793969847 | 69.61450952869981
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

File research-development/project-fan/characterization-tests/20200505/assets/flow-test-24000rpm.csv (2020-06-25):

t | p1_adc | patient | p2_adc | p2 | p3_adc | p3 | Q1
0.019 | 518.0 | 1.488833746898263 | 757.0 | 2.6683291770573567 | 746.0 | 2.6030150753768844 | 81.0173643874324
0.038 | 534.0 | 1.5682382133995036 | 787.0 | 2.8179551122194515 | 801.0 | 2.879396984924623 | 83.25789831176792
0.057 | 530.0 | 1.5483870967741935 | 708.0 | 2.423940149625935 | 717.0 | 2.457286432160804 | 77.21814323012694
0.076 | 3.725320496528184e-09 | -1.0818858560609166 | 737.0 | 2.56857855361596 | 744.0 | 2.592964824120603 | 79.48859750271231
0.094 | 526.0 | 1.5285359801488834 | 713.0 | 2.4488778054862843 | 704.0 | 2.391959798994975 | 77.61433948532223
0.113 | 505.0 | 1.4243176178660049 | 682.0 | 2.29426433915212 | 676.0 | 2.251256281407035 | 75.12424764860722
0.132 | 474.0 | 1.2704714640198511 | 705.0 | 2.4089775561097255 | 732.0 | 2.5326633165829144 | 76.97944669850344
0.151 | 505.0 | 1.4243176178660049 | 751.0 | 2.638403990024938 | 761.0 | 2.678391959798995 | 80.56178046992667
0.17 | 539.0 | 1.5930521091811414 | 752.0 | 2.6433915211970076 | 758.0 | 2.663316582914573 | 80.63788986854473
0.189 | 522.0 | 1.5086848635235732 | 674.0 | 2.254364089775561 | 700.0 | 2.371859296482412 | 74.46812811555122
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

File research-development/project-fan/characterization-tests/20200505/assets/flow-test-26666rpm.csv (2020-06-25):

t | p1_adc | patient | p2_adc | p2 | p3_adc | p3 | Q1
0.05 | 585.0 | 1.8213399503722085 | 838.0 | 3.0723192019950125 | 847.0 | 3.1105527638190953 | 86.93438295406521
0.15 | 618.0 | 1.9851116625310175 | 840.0 | 3.082294264339152 | 857.0 | 3.1608040201005023 | 87.0753958333687
0.2 | 559.0 | 1.6923076923076923 | 828.0 | 3.0224438902743143 | 850.0 | 3.1256281407035176 | 86.22585946185266
0.25 | 543.0 | 1.6129032258064515 | 835.0 | 3.057356608478803 | 840.0 | 3.0753768844221105 | 86.72243371644613
0.3 | 545.0 | 1.6228287841191067 | 744.0 | 2.603491271820449 | 736.0 | 2.5527638190954773 | 80.02698796478866
0.35 | 562.0 | 1.7071960297766748 | 847.0 | 3.117206982543641 | 848.0 | 3.1155778894472363 | 87.5671526847029
0.45 | 580.0 | 1.7965260545905708 | 826.0 | 3.0124688279301743 | 845.0 | 3.100502512562814 | 86.08345497249391
0.5 | 571.0 | 1.751861042183623 | 836.0 | 3.0623441396508726 | 845.0 | 3.100502512562814 | 86.79314097133647
0.55 | 574.0 | 1.7667493796526055 | 847.0 | 3.117206982543641 | 856.0 | 3.1557788944723617 | 87.5671526847029
0.6 | 559.0 | 1.6923076923076923 | 893.0 | 3.346633416458853 | 896.0 | 3.35678391959799 | 90.73241696209243
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

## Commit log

2020-04-12 Initial project creation
    [Alarms.SchDoc, Cycle-Controller.SchDoc, RespiraWorks Ventilator Rev 1.PcbDoc, RespiraWorks Ventilator.PrjPcb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]
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2020-04-14 added 12V dc-dc supply and cycle controller, level translators
    [Alarms.SchDoc, Cycle-Controller.SchDoc, Power.SchDoc, RespiraWorks Ventilator.PrjPcb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]
2020-04-15 adding discrete circuits, commit before annotation
    [Alarms.SchDoc, Power.SchDoc, RespiraWorks Ventilator Rev 1.PcbDoc, Sensors.SchDoc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]
2020-04-15 rough placement
    [Alarms.SchDoc, Cycle-Controller.SchDoc, Power.SchDoc, RespiraWorks Ventilator Rev 1.PcbDoc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]
2020-04-15 adding nightly outputs
    [RespiraWorks Ventilator Rev 1.PcbDoc, RespiraWorks Ventilator.PrjPcb]
2020-04-16 adding i2c pullups for issue #3
    [TOP.SchDoc]
2020-04-16 adding alarm LEDs issue #4
    [Alarms.SchDoc]
2020-04-16 added i2c multiplexer and 4 i2c sensor ports
    [Sensors.SchDoc]
2020-04-16 #5: retuned DC-DC for 1200khz, lower ripple and better derating on inductor
    [Power.SchDoc, Sensors.SchDoc]
2020-04-16 #15: changed heater connector to 3-pin to prevent mixup with solenoid connector.
    [Switches.SchDoc]
2020-04-16 #11 added PTC fuses to power outputs
    [Switches.SchDoc]
2020-04-16 #14: edge smoothing components for power switch gates
    [Switches.SchDoc]
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2020-04-19 nightly outputs for 4/18. switched cycle controller to STM32
    [Cycle-Controller.SchDoc, RespiraWorks Ventilator Rev 1.PcbDoc, RespiraWorks Ventilator.PrjPcb, Switches.SchDoc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]
2020-04-20 added series resistors to BJTs (#21)
    [Alarms.SchDoc]
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2020-04-21 removed reverse polarity input diode (#19)
    [Power.SchDoc, RespiraWorks Ventilator Rev 1.DRL, RespiraWorks Ventilator Rev 1.GBL, RespiraWorks Ventilator Rev 1.GBO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]
2020-04-21 analog scaling changed to 3.3V, fitler values and impedance maintained. #22
    [Sensors.SchDoc]
2020-04-21 added watchdog timer (#6), shifted cycle controller switch GPIOs to separate PWM timer outputs (#27)
    [Cycle-Controller.SchDoc, TOP.SchDoc, Watchdog.SchDoc]
2020-04-21 watchdog enable
    [TOP.SchDoc]
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2020-04-22 added SDcard slot (#24) and reshuffled PWM pins (#27), added ID pins (#17), removed rpi reset in favor of onboard WDT (#9)
    [Alarms.SchDoc, Cycle-Controller.SchDoc, Power.SchDoc, RespiraWorks Ventilator Rev 1.PcbDoc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]
2020-04-22 nightly outputs
    [RespiraWorks Ventilator Rev 1.DRL, RespiraWorks Ventilator Rev 1.GBL, RespiraWorks Ventilator Rev 1.GBO, RespiraWorks Ventilator Rev 1.GBP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]
2020-04-22 adding STEP file
    [20200421-NIGHTLY-RespiraWorks-Ventilator-3D-STEP.step, Power.SchDoc]
2020-04-22 #34: switched nucleo module to mechanical-only footprint with separate connectiors (similar to rpi)
    [Cycle-Controller.SchDoc, RespiraWorks Ventilator Rev 1.PcbDoc]
2020-04-22 #32, #33: switched UI <> Controller interface to controller USART3 and added flow control signals
    [Cycle-Controller.SchDoc, TOP.SchDoc]
2020-04-22 adding special nightly export
    [20200421v2-NIGHTLY-RespiraWorks-Ventilator-3D-STEP.step, Alarms.SchDoc, Cycle-Controller.SchDoc, Power.SchDoc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]
2020-04-23 switched buzzer selection
    [Alarms.SchDoc, Cycle-Controller.SchDoc, RespiraWorks Ventilator Rev 1.PcbDoc, RespiraWorks Ventilator.PrjPcb]
2020-04-23 #36: added bypass caps to power supply
    [Power.SchDoc]
2020-04-23 #22 corrected ADC scaling (5V inputs to 3.3V ADC)
    [Sensors.SchDoc]
2020-04-23 cleanup - switched CC ID to CC3V3 and added 5V power port for alarms block
    [Alarms.SchDoc, TOP.SchDoc]
2020-04-23 sync schematic blocks
    [TOP.SchDoc]
2020-04-23 added testpoints (#8), motor power connector (#38), and began placement
    [RespiraWorks Ventilator Rev 1.PcbDoc, TOP.SchDoc]
2020-04-23 nightly export
    [RespiraWorks Ventilator Rev 1.DRL, RespiraWorks Ventilator Rev 1.GBL, RespiraWorks Ventilator Rev 1.GBO, RespiraWorks Ventilator Rev 1.GBS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]
2020-04-23 converted 6.3V caps to 10V. Still X7R
    [Alarms.SchDoc, Cycle-Controller.SchDoc, Power.SchDoc, RespiraWorks Ventilator Rev 1.PcbDoc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]
2020-04-23 WIP placement
    [Cycle-Controller.SchDoc, RespiraWorks Ventilator Rev 1.PcbDoc, Switches.SchDoc, TOP.SchDoc]
2020-04-23 initial placement complete
    [Alarms.SchDoc, Cycle-Controller.SchDoc, Power.SchDoc, RespiraWorks Ventilator Rev 1.PcbDoc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]
2020-04-23 placement complete export for review
    [20200423v1-PLACEMENT-RespiraWorks-Ventilator-3D-STEP.step, RespiraWorks Ventilator Rev 1.DRL, RespiraWorks Ventilator Rev 1.GBL, RespiraWorks Ventilator Rev 1.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]
2020-04-23 layer stack and power planes
    [RespiraWorks Ventilator Rev 1.PcbDoc, Sensors.SchDoc]
2020-04-23 Top power section polygons
    [Power.SchDoc, RespiraWorks Ventilator Rev 1.PcbDoc]
2020-04-23 export for WIP layout
    [RespiraWorks Ventilator Rev 1.DRL, RespiraWorks Ventilator Rev 1.GBL, RespiraWorks Ventilator Rev 1.GTL, RespiraWorks Ventilator Rev 1.GTO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]
2020-04-24 routing, fixed #47
    [Cycle-Controller.SchDoc, RespiraWorks Ventilator Rev 1.PcbDoc, Sensors.SchDoc]
2020-04-24 #44 implemented pin swaps to accommodate option of using X-NUCLEO-IHM03A1 powerSTEP01 stepper driver board
    [Cycle-Controller.SchDoc, RespiraWorks Ventilator.PrjPcb, TOP.SchDoc]
2020-04-24 i2c routing complete
    [Cycle-Controller.SchDoc, RespiraWorks Ventilator Rev 1.PcbDoc, RespiraWorks Ventilator.PrjPcb]
2020-04-24 DRC zero
    [Cycle-Controller.SchDoc, RespiraWorks Ventilator Rev 1.PcbDoc, RespiraWorks Ventilator.PrjPcb, UI-Computer.SchDoc]
2020-04-24 review export
    [20200423v3-REVIEW-RespiraWorks-Ventilator-3D-STEP.step, 20200423v3-REVIEW-RespiraWorks-Ventilator-ASSY-BOM.xls, Cycle-Controller.SchDoc, RespiraWorks Ventilato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]
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2020-04-25 added ground plane stitches #50
    [RespiraWorks Ventilator Rev 1.PcbDoc]
2020-04-25 added individual voltage setting resistors for each i2c sensor port #52
    [RespiraWorks Ventilator Rev 1.PcbDoc, Sensors.SchDoc, TOP.SchDoc]
2020-04-25 added mech parts to schematic for BOM purposes #46
    [Cycle-Controller.SchDoc, RespiraWorks Ventilator.PrjPcb, TOP.SchDoc, UI-Computer.SchDoc]
2020-04-25 swapped for locking power connector (#37), prep for manufacturing
    [Power.SchDoc, RespiraWorks Ventilator Rev 1.PcbDoc, Watchdog.SchDoc]
2020-04-25 created turnkey fab package for Release Candidate 1
    [20200424v1-RespiraWorks-Ventilator-Rev1.0-RC1-3D-STEP.step]
2020-04-25 #53 switched D5 and D6 to SE30AFG-M3/6A
    [Alarms.SchDoc, RespiraWorks Ventilator Rev 1.DRL, RespiraWorks Ventilator Rev 1.GBL, RespiraWorks Ventilator Rev 1.GBO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]
2020-04-25 creating RC2 to correct #53
    [20200424v2-RespiraWorks-Ventilator-Rev1.0-RC2-3D-STEP.step, 20200424v2-RespiraWorks-Ventilator-Rev1.0-RC2-ASSY-BOM.xls, Power.SchDoc]
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2020-05-10 Add files via upload
    Extended inlet to improve flow response, throat expanded to 5.4mm
    [[Flow Measurement Venturi - 10-32 Style] v3.iges]
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2020-05-17 Updates general README with new structure + couple other fixes
    [[Flow Measurement Venturi - 10-32 Style] v3.iges, [Flow Measurement Venturi - 10-32 Style] v3.step, [Flow Measurement Venturi - 10-32 Style] v4.f3d, exhaust pi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]
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2020-05-19 updating comments and fixing compile issues with reference design import
    [Alarms.SchDoc, Cycle-Controller-Onboard.SchDoc, RespiraWorks Ventilator.PrjPcb, ST-LINK.SchDoc]
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2020-05-27 fixed directory case
    [exhaust pinch valve 1.6 - base.step, exhaust pinch valve 1.6 - bearing.step, exhaust pinch valve 1.6 - rotor.step, venturi-3-4.f3d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]
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2020-06-02 Updates folder names for project-venturi & pneumatic-system to fix root readme broken links
    [venturi-3-4.f3d, venturi-3-4.iges, venturi-5-8.f3d, venturi-5-8.iges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]
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2020-06-25 Run pre-commit on system-design folder.
    Mostly fixing end-of-while whitespace.
    [venturi-5-8.step]
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2020-07-20 Adds consolidated CoVent links to root README
    Puts software in its own folder; Updates root README
    Moves system-design folder contents into repo root
    adds pre-commit formatting
    Fixes borked links
    fixes more borked links
    Converts PCBreathe & SysDesign repo links
    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
    [2020-05-14-pip15-peep5-rr12-ie23.csv, 2020-05-14-pip25-peep10-rr12-ie23.csv, 2020-05-14-vent-off.csv, 2020-06-06-QuickLung-FMLtest-InspireEffort-2strong-2mediu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]
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2020-08-08 DNP'd C33 and C34 per issue 846 (#848)
    * DNP'd C33 and C34 per issue 846
    * removed broken ephemeral ebay link
    [RespiraWorks Ventilator.PrjPcb, Switches.SchDoc]
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2020-08-12 WIP filter BOM
    added photos and instructions, 3d print files
    spelling error
    some cleanup and made discoverable
    assets folder and nicer layout of pictures
    [SmallFilterHousing.stl, SmallFilterPatientConnector.stl, filter-gasket-jig-inside.stl, filter-gasket-jig-outsideLarge.stl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]
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2021-02-18 tweaked barb end, will need to fix alignment
    [u_bend_tubing_adapter.ipt]
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2021-02-19 fixed issue with configuration rebuild
    [u_bend_tubing_adapter.ipt]
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2021-06-25 pinch valve rotor shaft clearance reparametrized, multiple STL exports
    [pinch_valve_assembly.iam, pinch_valve_rotor.ipt, pinch_valve_rotor.stl, pinch_valve_rotor_008.stl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]

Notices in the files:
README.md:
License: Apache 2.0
